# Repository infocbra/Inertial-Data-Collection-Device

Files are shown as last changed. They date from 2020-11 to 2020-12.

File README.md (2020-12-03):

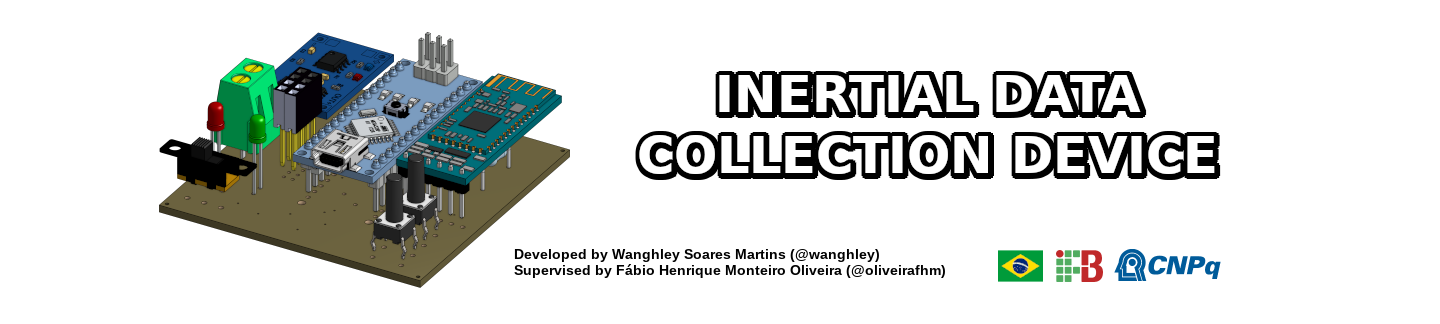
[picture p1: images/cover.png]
Inertial Data Collection Device






>  printed circuit board and code for collecting inertial data to research purposes of movements.

## About
Hardware developed to collect inertial data of humans (i.e. Accelerometer, Giroscope) and temperature in order to provide an open source hardware for researchs related to the analysis of human movements for many purposes.<br>
This project was tested in the diagnosis and prognosis of neuromotor diseases - Parkinson's disease mostly as part of the project of scientific research [**"Visualization Strategies to Online Big Data applied in individualized medicine"**](https://github.com/Wanghley/PIBIC-Strategies-Data-Visualization-Medicine).

## Requirements
| Dependency | Platform | Description |
| :--------- | -------- | :---------- |
| [arduino_2012](https://github.com/Wanghley/Inertial-Data-Collection-Device/blob/main/lib/arduino_2012.lbr) | eagle lib | arduino schematic and layout to **Eagle** project |
| [con-headers-jp](https://github.com/Wanghley/Inertial-Data-Collection-Device/blob/main/lib/con-headers-jp.lbr) | eagle lib | schematic and layout of female pin bars to **Eagle** project |
| [DIY modules](https://github.com/Wanghley/Inertial-Data-Collection-Device/blob/main/lib/diy-modules.lbr) | eagle lib | bluetooth adaptor fotoprint and symbol to **Eagle** project |
| [KRE](https://github.com/Wanghley/Inertial-Data-Collection-Device/blob/main/lib/kre.lbr) | eagle lib | borne connector fotoprint and symbol to **Eagle** project |
| [pinhead](https://github.com/Wanghley/Inertial-Data-Collection-Device/blob/main/lib/pinhead.lbr) | eagle lib | added in the **Eagle** project for auxiliary view of pin bars |
| [TimerOne 1.1.0](https://github.com/Wanghley/Inertial-Data-Collection-Device/blob/main/lib/TimerOne-1.1.0.zip) | arduino lib | allow running a periodic interrupt function based in finer PWM control |
| [MPU6050 0.2.1](https://github.com/Wanghley/Inertial-Data-Collection-Device/blob/main/lib/MPU6050-0.2.1.zip) | arduino lib | allow MPU6050 easy control and manipulation |
| [Wire](https://www.arduino.cc/en/reference/wire) | arduino lib | allow communication over I2C protocol |
| [SoftwareSerial](https://www.arduino.cc/en/Reference/softwareSerial) | arduino lib | allow serial communication on other digital pins of the Arduino |

## Bill of Materials
| # | Designator | Qty | Description | Obs |
| - | :--------- | --- | :---------- | :---------- | 
| 1 | R1, R2 | 2 | Resistor 220R 5% (1/4W) | Used for digital protection of bluetooth module RX |
| 2 | HC-05 | 1 | HC-05 Bluetooth Module | Module of Low supply consumption for prototype communication |
| 3 | PUSH | 2 | Push Button Long Head | Push button for hardware control and operation  |
| 4 | ON/OFF | 1 | 255sb sliding switch | Sliding switch to control energy supply of the prototype |
| 5 | LED1 | 1 | COM-09590 | 2.25 V Red LED 5mm Cylindrical indicates the hardware is ready for collection |
| 6 | LED2 | 1 | COM-09590 | 2.25 V green LED 5mm Cylindrical indicates the hardware operation mode and collection in process |
| 6 | Arduino Nano | Arduino Nano | | mother board and controller |
| 7 | KRE-2P | 1 | Borne Connector | Connector to the batery |
| 8 | BATTERY CHARGER | 1 | TP4056 | Power supply adn voltage regulator to the batery |

## Development
In order to run and contribute to the PCB development you must have **Eagle**  installed in your computer and then use the .sch to work on the circuit itself and the .brd to work in the layout design.

Now, for the development under de code of hardware control you must have Arduino IDE or similar to work on the .ino code.

## Authors
*   **Wanghley Soares Martins** - *junior researcher* - [wanghley](https://github.com/wanghley)
*   **Fábio Henrique Monteiro Oliveira** - *research advisor* - [oliveirafhm](https://github.com/oliveirafhm)

See also the list of [contributors](https://github.com/Wanghley/PIBIC-Strategies-Data-Visualization-Medicine/contributors) who participated in this project.

## License
This project is licensed under the MIT License - see the [LICENSE.md](LICENSE.md) file for details

## Acknowledge
*   Remember, the project is free for you to use, manipulate, change and distribute. However, I am just asking you to mention us in any copy, modification as the root of your development.
*   I would advice you to try out the hardware with an analysis of the result data.
*   If you want an easier software for hardware control, check out the [CONTROL SOFTWARE](https://github.com/Wanghley/PIBIC-Strategies-Data-Visualization-Medicine)

## Gallery
General view of the projected PCB. For more images go to [images/](https://github.com/Wanghley/Inertial-Data-Collection-Device/tree/main/images) and if you still want to see more you can see 3D views on [view/](https://github.com/Wanghley/Inertial-Data-Collection-Device/tree/main/view)
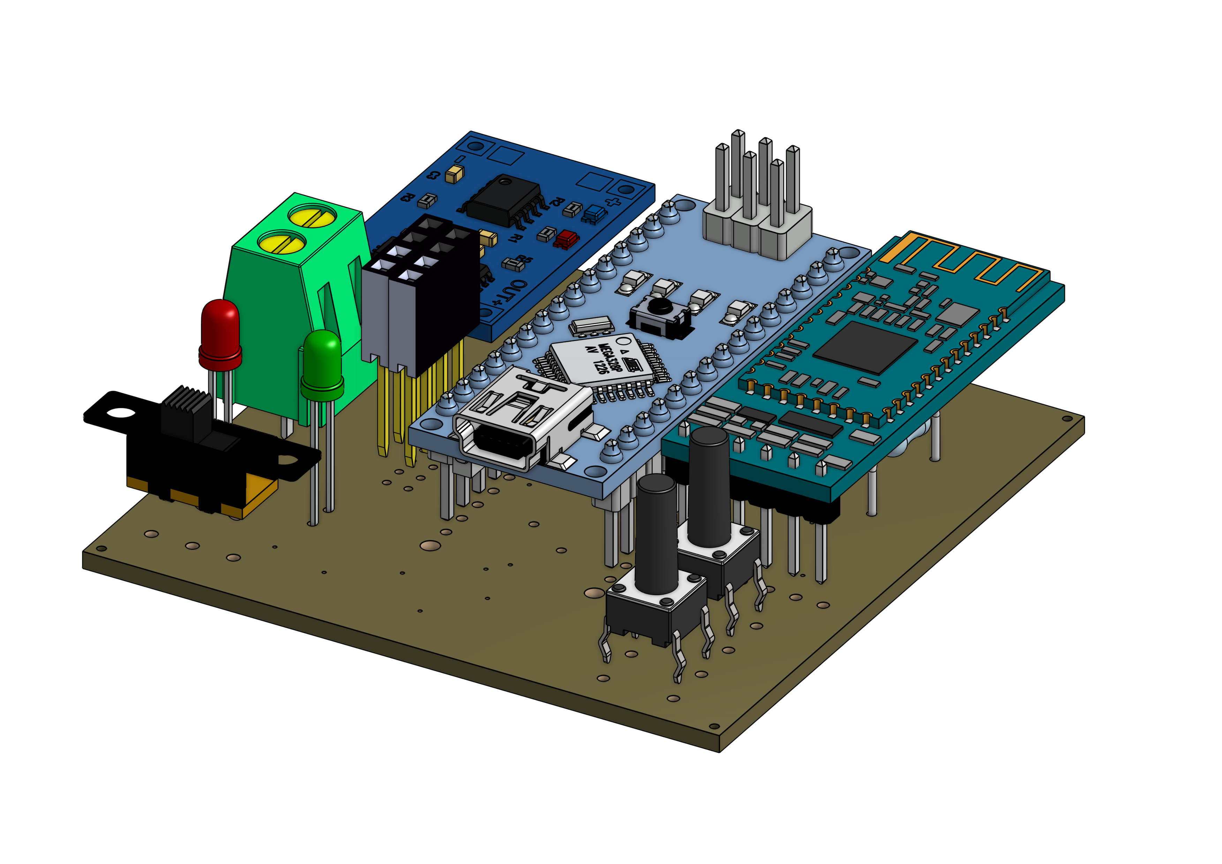
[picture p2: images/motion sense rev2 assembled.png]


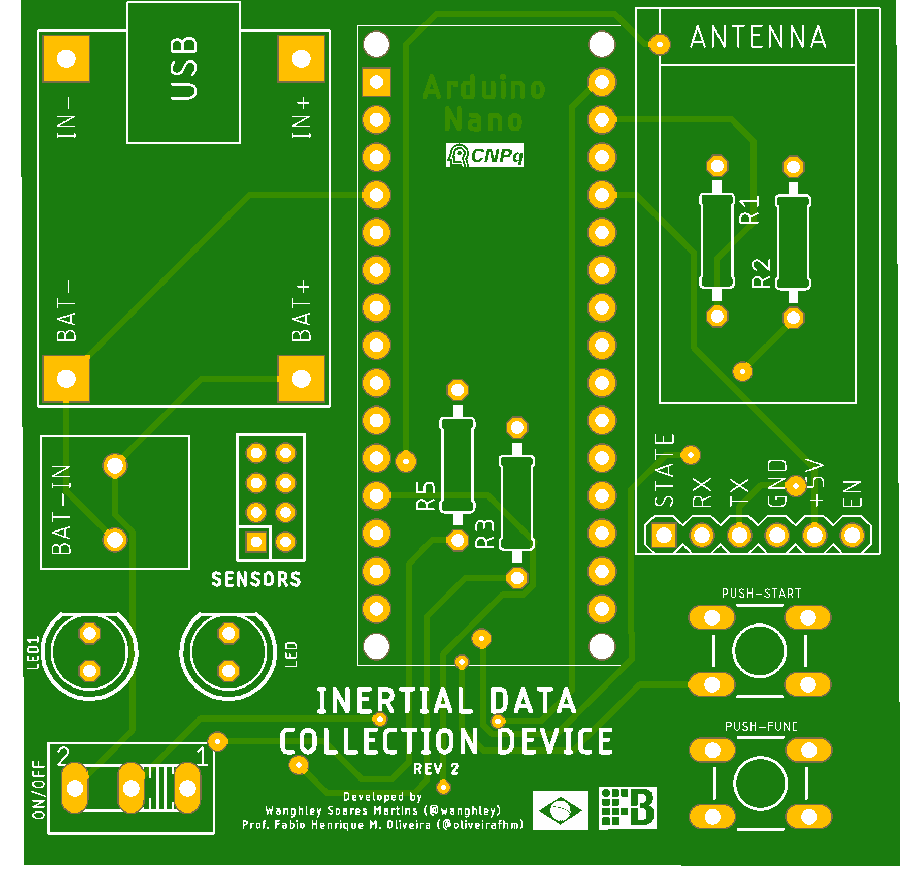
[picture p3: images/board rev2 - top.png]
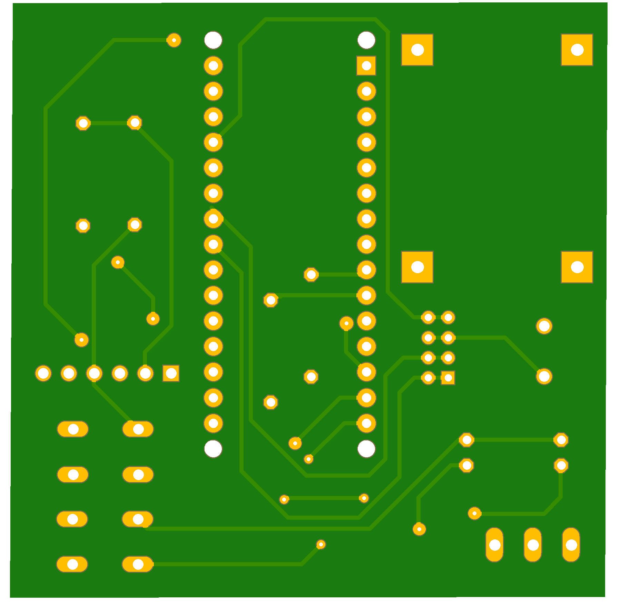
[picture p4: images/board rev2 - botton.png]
|  | | 
|-|-|

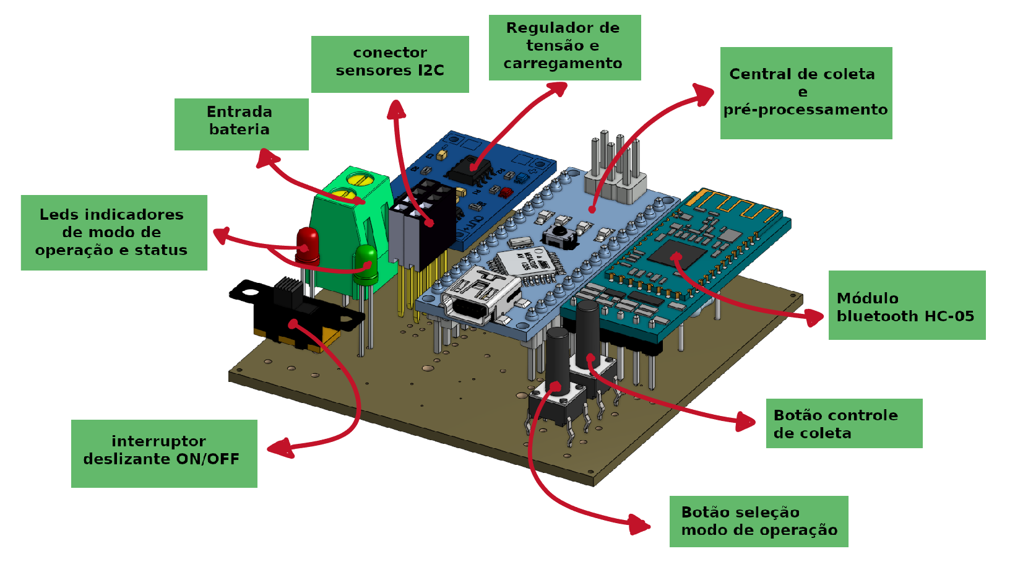
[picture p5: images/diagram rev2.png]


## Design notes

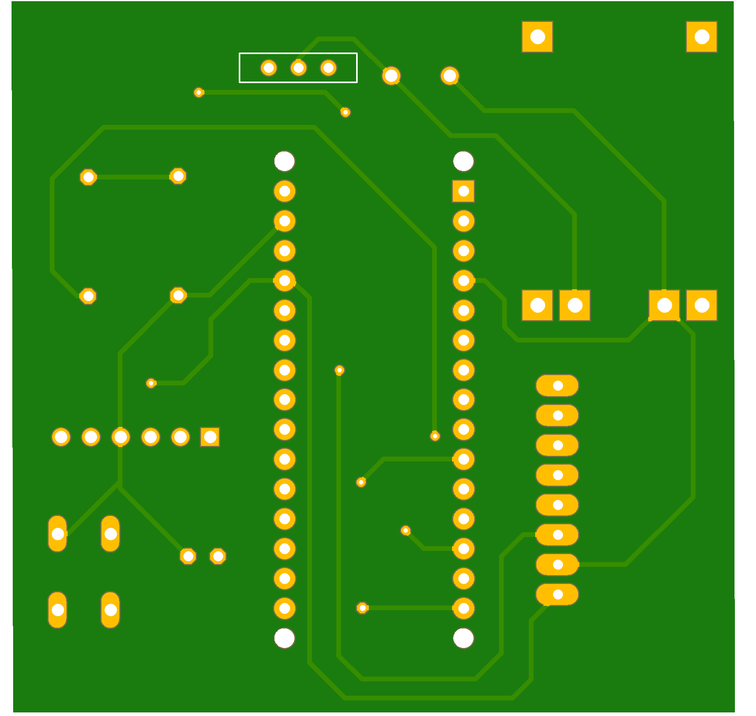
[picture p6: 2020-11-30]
images/board rev1 - botton.png

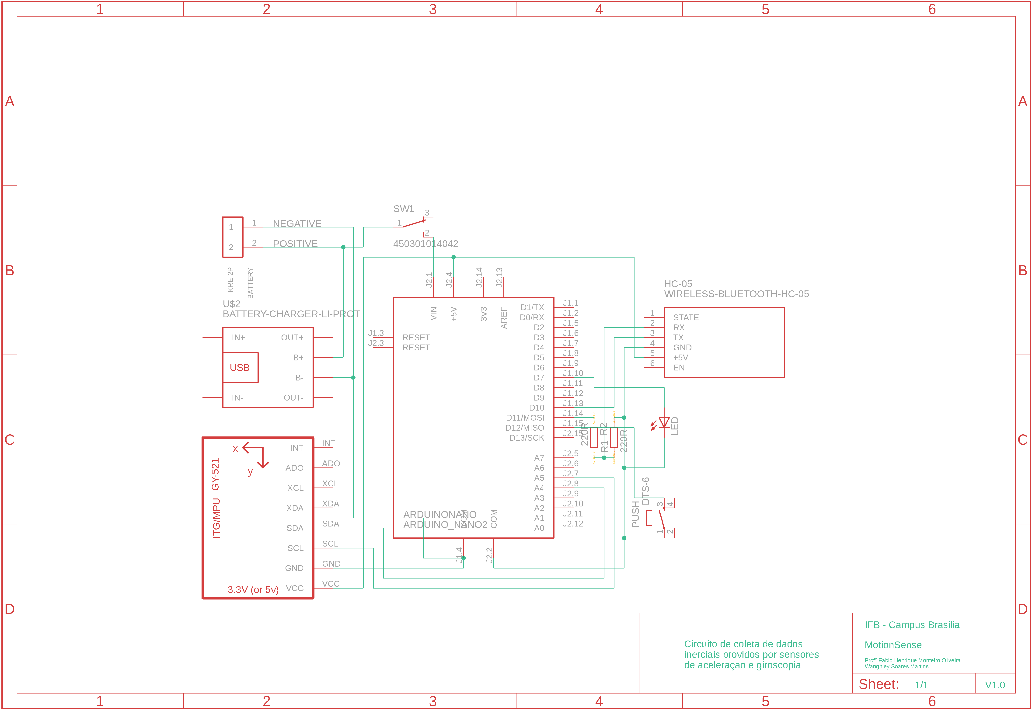
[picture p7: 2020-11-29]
images/sch rev1.png

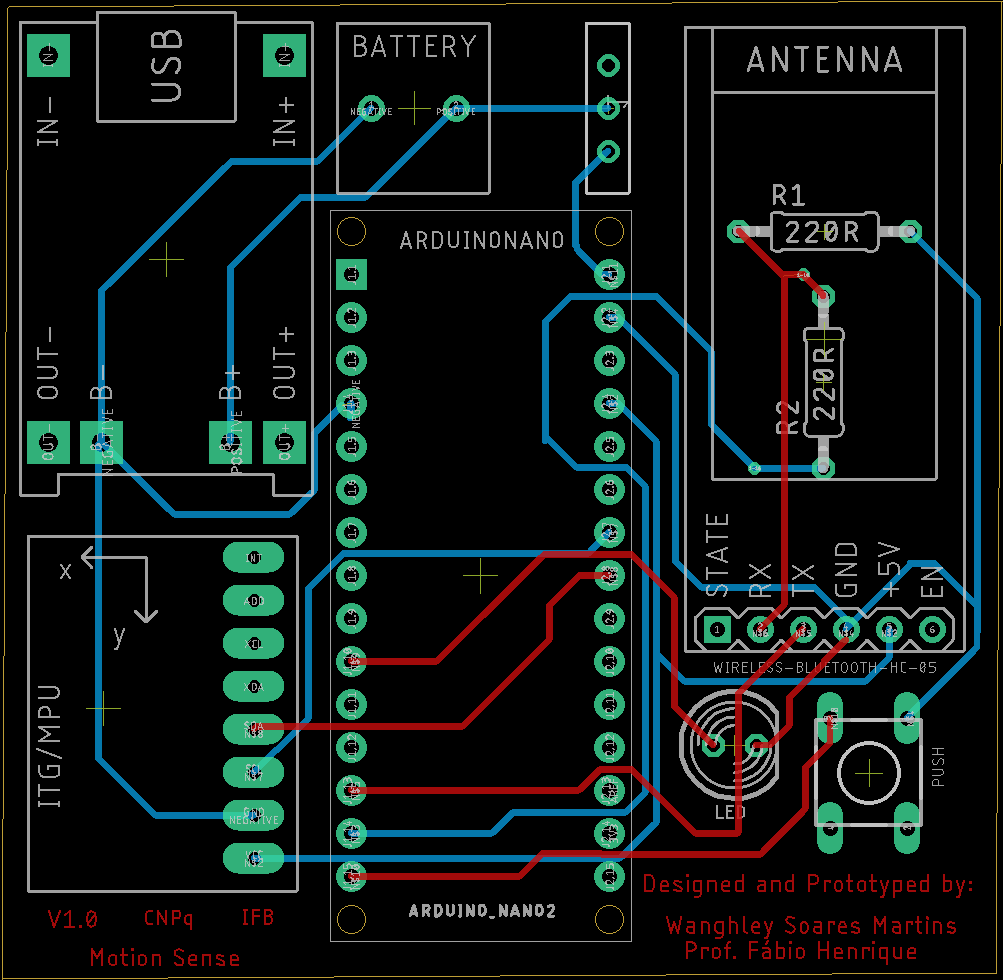
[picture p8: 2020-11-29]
images/pcb rev1.png

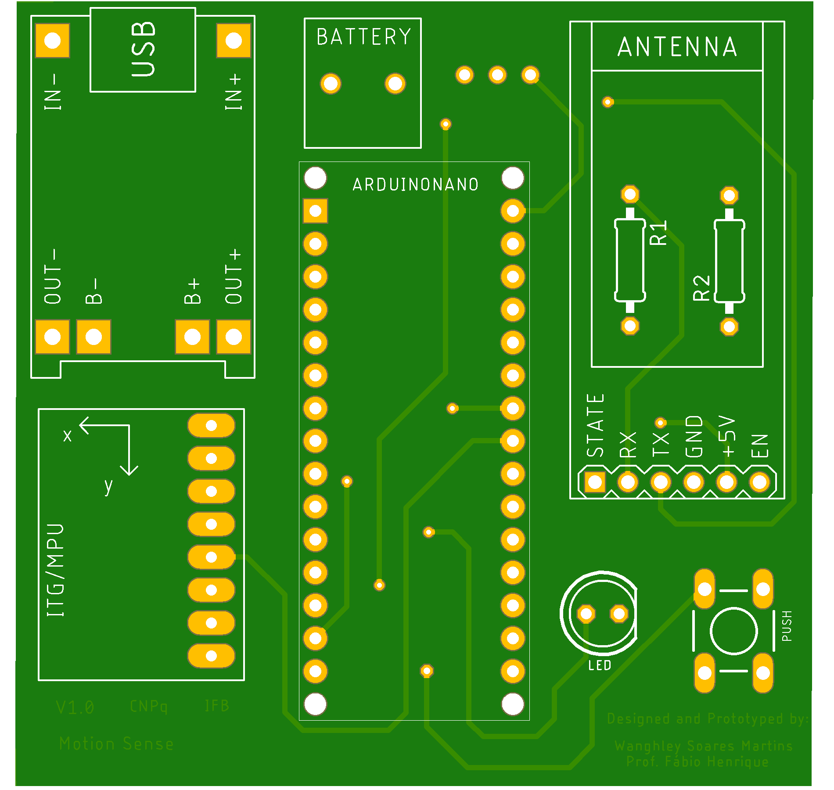
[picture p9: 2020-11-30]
images/board rev1 - top.png

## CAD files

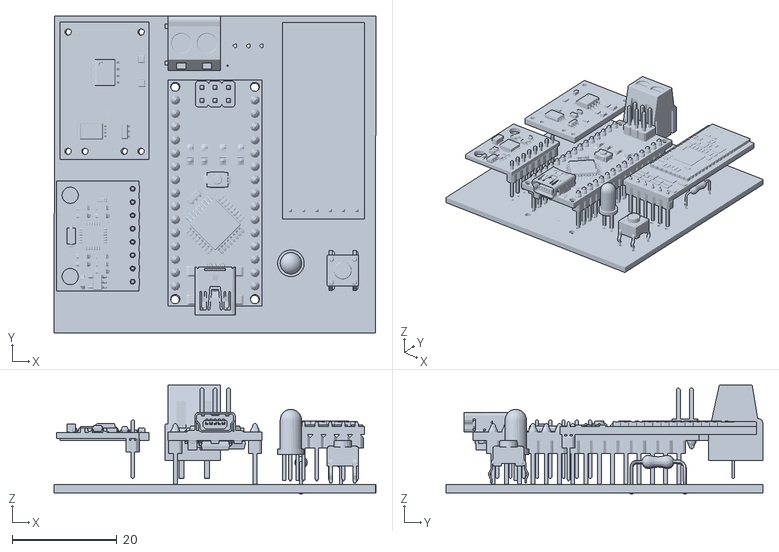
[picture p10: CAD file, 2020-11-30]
view/motion sense rev1 HQ.stl
61.6 x 60.6 x 20.8

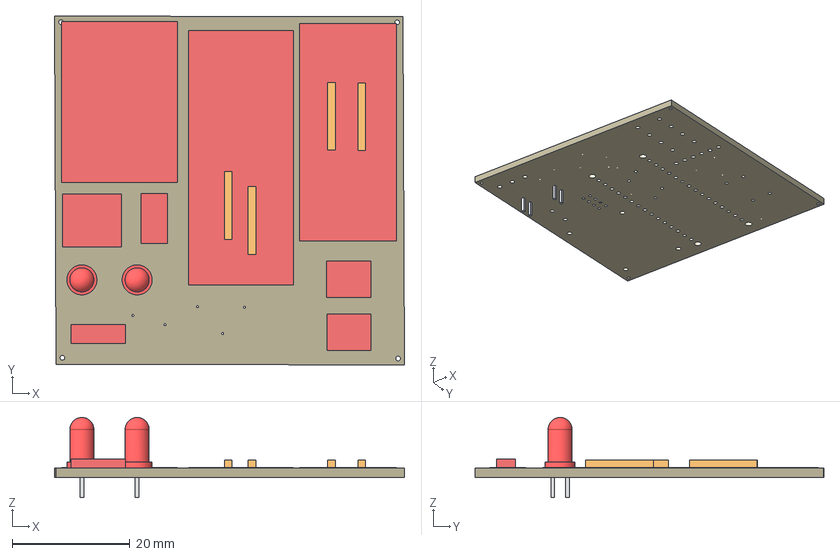
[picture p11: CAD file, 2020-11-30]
view/pcb-only.step
59.4 x 59.2 x 13.6 mm
Board
WIRELESS-BLUETOOTH-HC-05
collection indicator x 2
DTS-6 x 2
330R x 4
BATTERY-CHARGER-LI-5V
F-2X04-DIL-2MM_M
KRE-2P
255SB
ARDUINO_NANO2

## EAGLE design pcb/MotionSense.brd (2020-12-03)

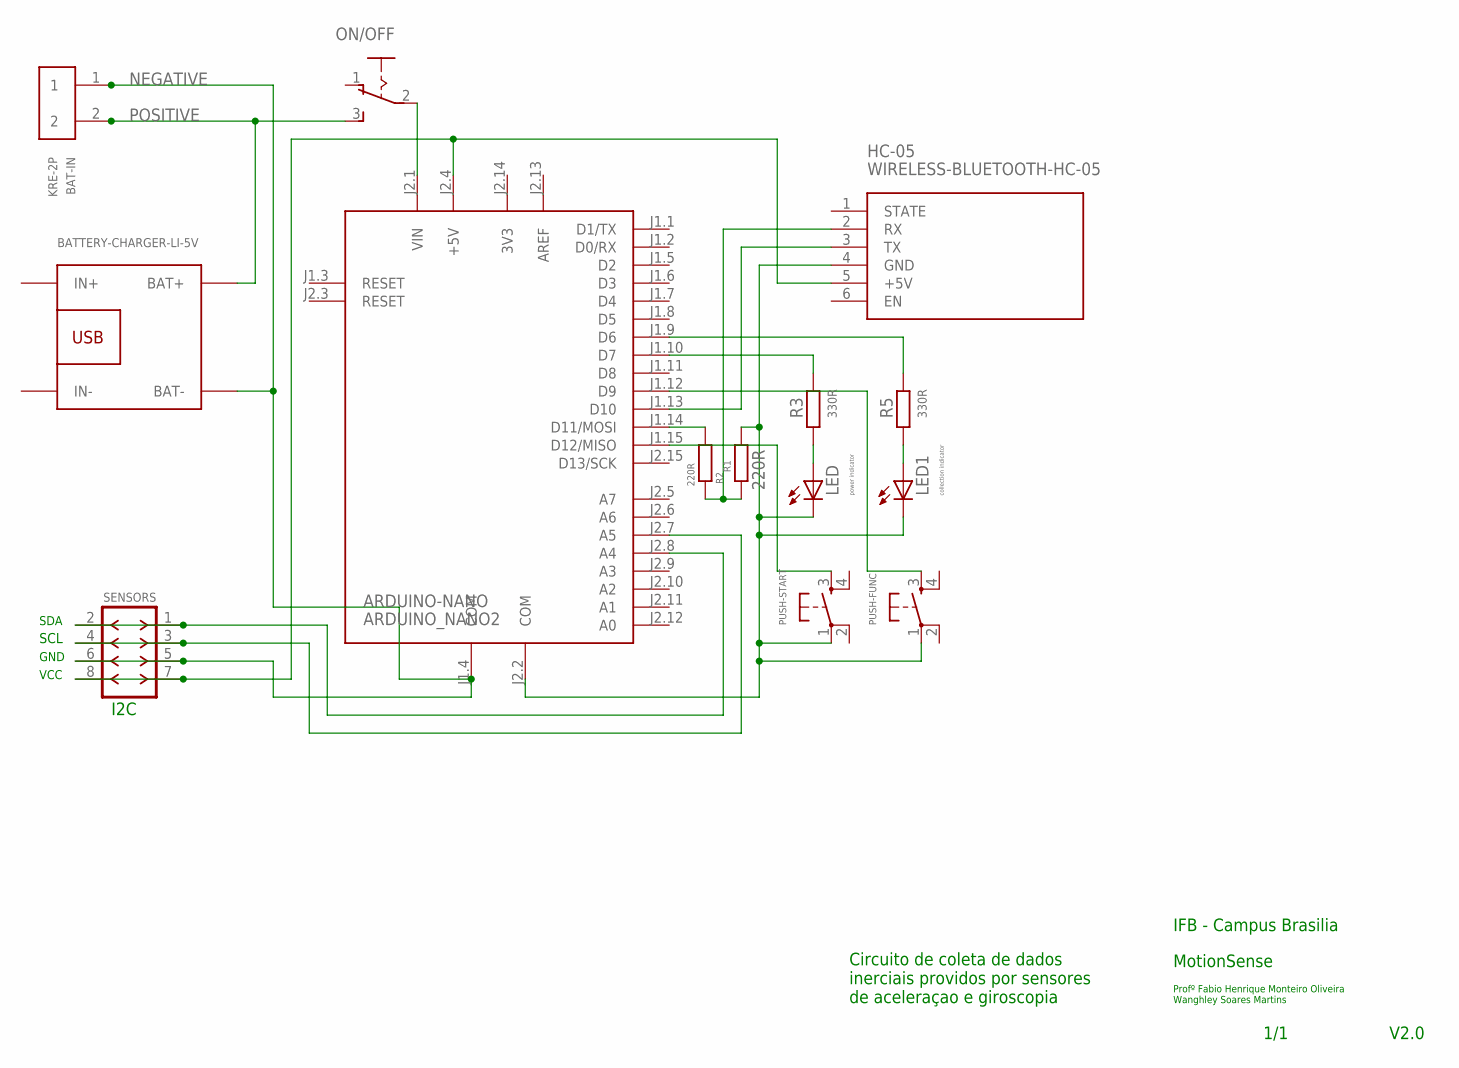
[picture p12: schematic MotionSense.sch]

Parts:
ARDUINO-NANO: ARDUINO_NANO2
BAT-IN: KRE-2P
HC-05: WIRELESS-BLUETOOTH-HC-05
LED: power indicator; LED5MM
LED1: collection indicator; LED5MM
ON/OFF: 255SB
PUSH-FUNC: DTS-6
PUSH-START: DTS-6
R1, R2: 220R; 0207/10
R3, R5: 330R; 0207/10
SENSORS: F-2X04-DIL-2MM_M; DIL-2MM-2X04_M
U$1: BATTERY-CHARGER-LI-5V

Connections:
3V3: ARDUINO-NANO.J2.14 (3V3)
AREF: ARDUINO-NANO.J2.13 (AREF)
unnamed: LED.A, R3.1
unnamed: ARDUINO-NANO.J2.4 (+5V), HC-05.5 (+5V), SENSORS.7, SENSORS.8
unnamed: ARDUINO-NANO.J1.14 (D11/MOSI), R2.1
unnamed: ARDUINO-NANO.J2.2 (COM), HC-05.4 (GND), LED.K (C), LED1.K (C), PUSH-FUNC.1, PUSH-START.1, R1.2
unnamed: ARDUINO-NANO.J1.13 (D10), HC-05.3 (TX)
unnamed: HC-05.2 (RX), R1.1, R2.2
unnamed: ARDUINO-NANO.J2.7 (A5), SENSORS.3, SENSORS.4
unnamed: ARDUINO-NANO.J2.8 (A4), SENSORS.1, SENSORS.2
unnamed: ARDUINO-NANO.J1.10 (D7), R3.2
unnamed: ARDUINO-NANO.J1.15 (D12/MISO), PUSH-START.3
unnamed: ARDUINO-NANO.J2.1 (VIN), ON/OFF.2
unnamed: ARDUINO-NANO.J1.12 (D9), PUSH-FUNC.3
unnamed: ARDUINO-NANO.J1.9 (D6), R5.2
unnamed: LED1.A, R5.1
NEGATIVE: ARDUINO-NANO.J1.4 (COM), BAT-IN.1, SENSORS.5, SENSORS.6, U$1.BAT-
POSITIVE: BAT-IN.2, ON/OFF.3 (S), U$1.BAT+

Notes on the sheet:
Circuito de coleta de dados inerciais providos por sensores de aceleraçao e giroscopia
MotionSense
IFB - Campus Brasilia
Profº Fabio Henrique Monteiro Oliveira Wanghley Soares Martins
V2.0
1/1
I2C
VCC
GND
SCL
SDA

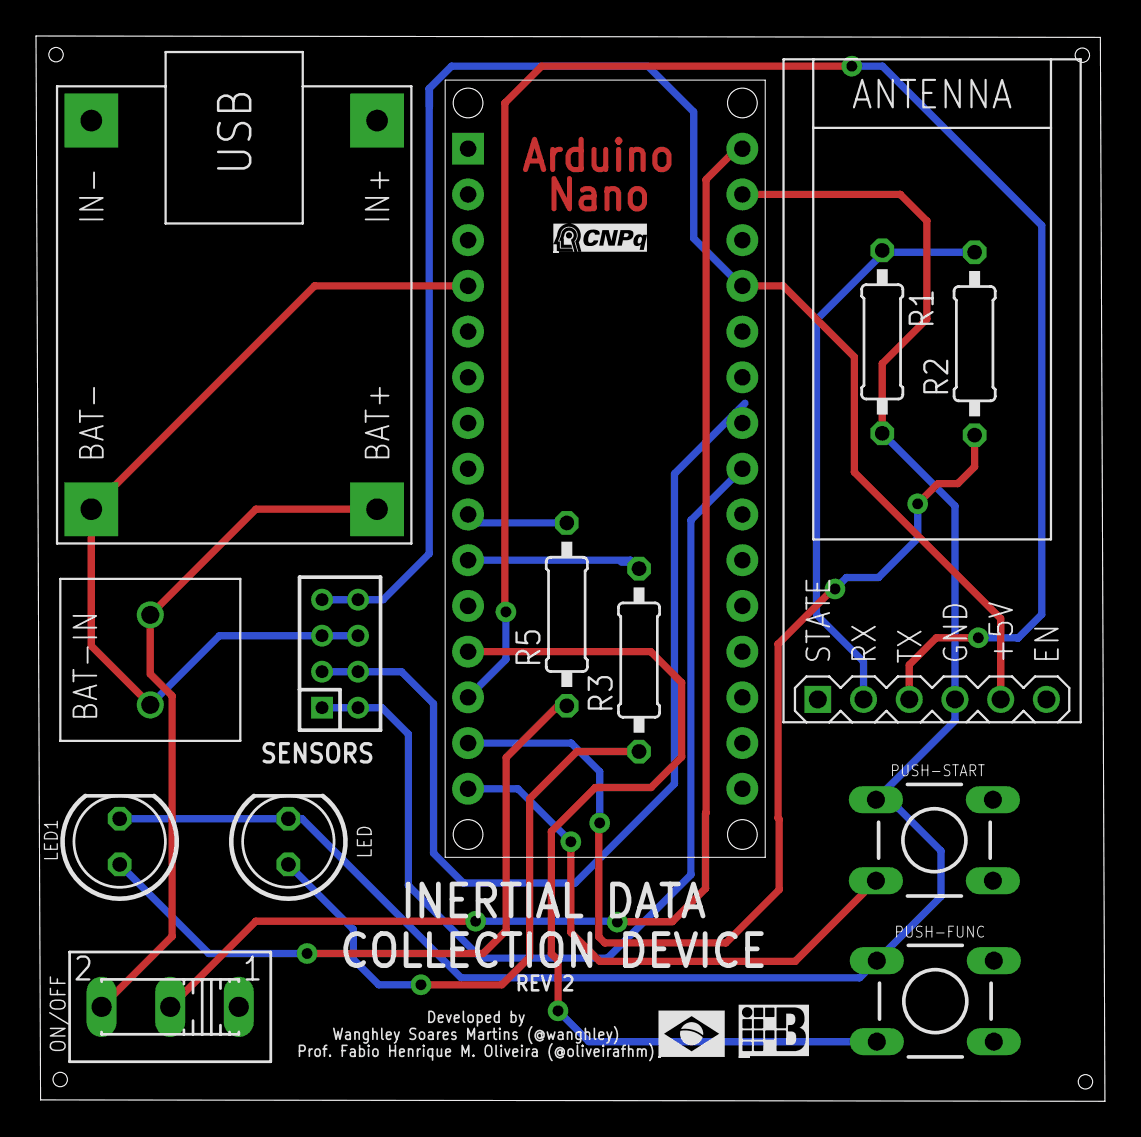
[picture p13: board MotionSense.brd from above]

Board: 2 copper layers, 59.4 x 59.2 mm, 14 parts (0 on the bottom side), 16 nets.

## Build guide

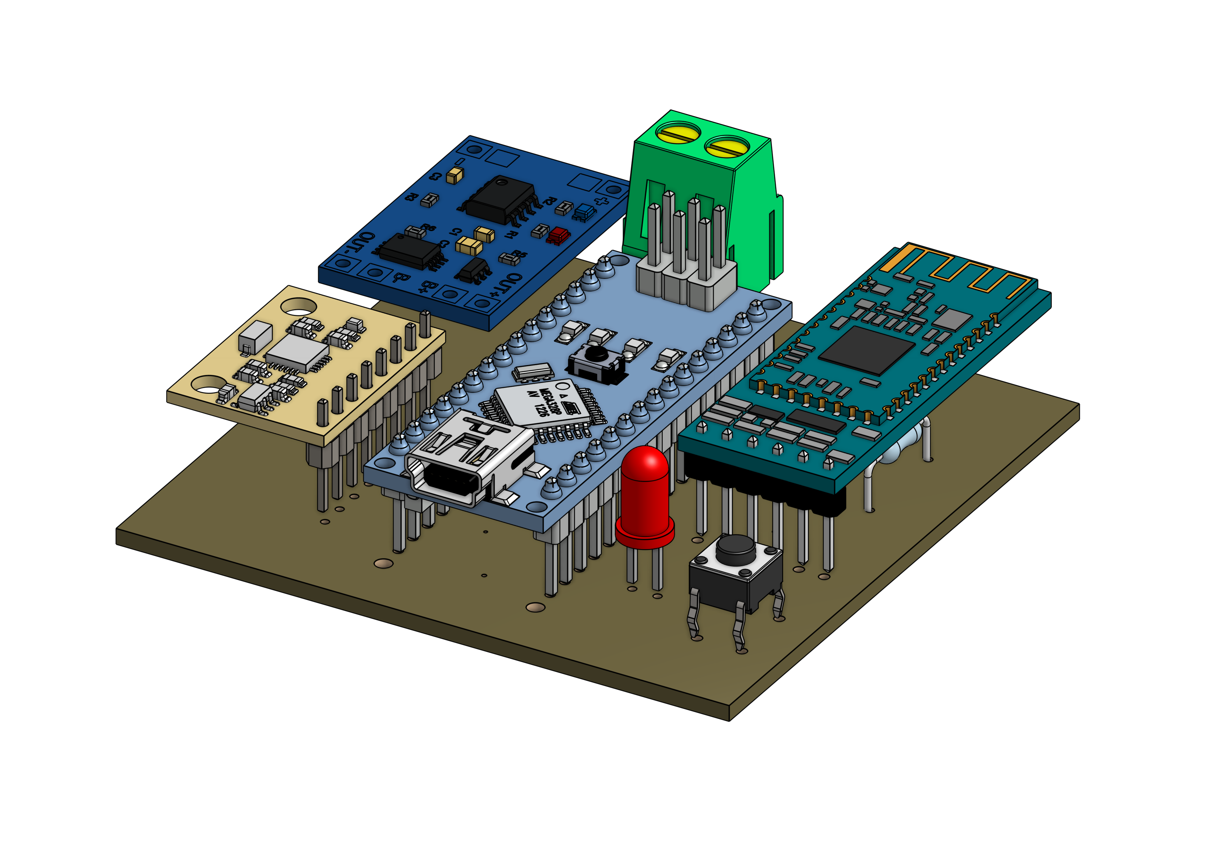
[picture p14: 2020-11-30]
images/motion sense rev1 assembled.png

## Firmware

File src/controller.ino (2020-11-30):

/*
AUTHOR: Wanghley Soares Martins (@wanghley)
DATE: April 11, 2019
CONTACT: wanghleys@gmail.com
REV1: Fabio Henrique, Lissa Ximenes
DATE: Sep 19, 2019
REV2: Wanghley Martins
DATE: Nov 19, 2020
*/
#include <TimerOne.h>       // Library for timer interrupt
#include <MPU6050.h>        // Standard library for manipulation on the MPU6050
#include <Wire.h>           // Control library of the I²C protocol, used by the MPU6050
#include <SoftwareSerial.h> // Bluetooth control library

#define BTN 12
#define LED 7

SoftwareSerial BTSerial(10, 11); // RX | TX

const int MPU = 0x68; // MPU6050 address on the I²C bus (available in datasheet)
volatile bool visualization = false; // Variable is loaded into the "RAM memory" of the microcontroller
boolean controle = true, initiate = false; // Variable of flow control
int ledstate = 0; // LED state indicator
double AcX, AcY, AcZ, Tmp, GyX, GyY, GyZ; // Variables used to store data
char a, c='-1', c1='-1';
unsigned long current;
unsigned long last;
volatile bool flag = false;
bool flagCopy;
volatile unsigned long interval = 0;
unsigned long intervalCopy;
long Micros;

void setup()
{
    /*Bluetooth comunication: 
      Module - HC-05
      Password - 1234
    */
    Wire.begin();                // I²C communication starts
    Wire.beginTransmission(MPU); // Indicates the address of the MPU to start communication
    Wire.write(0x6B);            // Indicates the MPU that the communication will start
    Wire.write(0);               // Indicates the MPU that wants to leave the communication on standby
    Wire.endTransmission(true);  // Disables communication

    Serial.begin(57600);
    Serial.println("Open Parkinson's Diagnostic Device");
    BTSerial.begin(57600); // HC-05 default speed in AT command more

    // starts the sample rate by time (clock)
    Timer1.initialize(20000); // Adjusted for 50hz = 10⁶ / 50 = 20,000µs
    Timer1.attachInterrupt(changeFlag); // Indicates the function that will be called every 20,000ms
    
    pinMode(BTN,INPUT_PULLUP);
    pinMode(LED,OUTPUT);
    digitalWrite(LED,LOW);
}

//Função que imprime os dados lidos pelo MPU6050 a cada chamada da interrupção
void changeFlag(){
  if (visualization){
    flag = true; // active data display
    Micros = micros();
  }    
}

void loop(){
  if(digitalRead(BTN)==LOW){
   if(initiate==true){
     Serial.println("Finalizando...");
     initiate = false;
     BTSerial.write("stop#");
     digitalWrite(LED,LOW);
   }else{
     Serial.println("initiatendo...");
     initiate=true;
     digitalWrite(LED,HIGH);
   }
   delay(350);
  }
    
  if (initiate){ 
    if(Serial.available()){
     a = Serial.read();
     if(a=='f'){
       BTSerial.write("stop#");
       BTSerial.flush();//Descarrega o buffer
       Serial.println("Comunication Closed!");
       visualization = false;
     }
    }

    noInterrupts();// 
    flagCopy = flag;
    flag = false;
    intervalCopy = interval;
    interval = 0;
    interrupts();
    if (flagCopy){
      printData();
    }
    int val = BTSerial.read();
    
    c='-1';
    c1='-1';
    if (val != -1){
        c = val;
    }
    
    if (c == 's'){
      Serial.println("Comunication started!\nWaiting final handshake");
      BTSerial.write("ok#");
      BTSerial.flush(); //Limpar buffer
      while (controle){
        val = BTSerial.read();
        if (val != -1){
          c1 = val;
          if(c1=='c'){
            controle = false;
            Serial.println("Data collection started!");
            visualization = true;
          }
        }
      }
    }
    
    if (visualization){
        Wire.beginTransmission(MPU); //Indica a retomada na comunicação i²c
        Wire.write(0x3B);            /*initiate o registrador do MPU6050, indicando que irá receber dados*/
        Wire.endTransmission(false); //initiate a comunicação estável novamente
        //Solicita dados do sensor
        Wire.requestFrom(MPU, 14, true);
        getData();
        // Keep reading from HC-05 and send to Arduino Serial Monitor
    }

    if (Serial.available()){
      a = Serial.read();
      if (a == 'f'){
        BTSerial.write("stop#");
        BTSerial.flush(); //Descarrega o buffer
        Serial.println("Canal fechado..");
        visualization = false;
      }
    }
  }
}

//Função que recebe os dados do MPU6050 e
//faz as conversões do valor bruto para acc = g e gy = º/seg
void getData(){
  //Armazena o valor dos sensores nas variaveis correspondentes
  AcX = Wire.read() << 8 | Wire.read(); //0x3B (ACCEL_XOUT_H) & 0x3C (ACCEL_XOUT_L)
  AcY = Wire.read() << 8 | Wire.read(); //0x3D (ACCEL_YOUT_H) & 0x3E (ACCEL_YOUT_L)
  AcZ = Wire.read() << 8 | Wire.read(); //0x3F (ACCEL_ZOUT_H) & 0x40 (ACCEL_ZOUT_L)
  Tmp = Wire.read() << 8 | Wire.read(); //0x41 (TEMP_OUT_H) & 0x42 (TEMP_OUT_L)
  GyX = Wire.read() << 8 | Wire.read(); //0x43 (GYRO_XOUT_H) & 0x44 (GYRO_XOUT_L)
  GyY = Wire.read() << 8 | Wire.read(); //0x45 (GYRO_YOUT_H) & 0x46 (GYRO_YOUT_L)
  GyZ = Wire.read() << 8 | Wire.read(); //0x47 (GYRO_ZOUT_H) & 0x48 (GYRO_ZOUT_L)
  
  
  //Dados recebidos em 2g
  AcX = AcX / 16384.0;        //Conversão para G
  AcY = AcY / 16384.0;        //Conversão para G
  AcZ = AcZ / 16384.0;        //Conversão para G
  Tmp = Tmp / 340.00 + 36.53; //Conversão para ºC
  GyX = GyX / 250.0;          //Conversão para º/seg
  GyY = GyY / 250.0;          //Conversão para º/seg
  GyZ = GyZ / 250.0;          //Conversão para º/seg
}

void printData(){
  BTSerial.print((String)Micros+","+(String)AcX+","+(String)AcY+","+(String)AcZ+","+(String)GyX+","+(String)GyY+","+(String)GyZ+","+(String)Tmp+"#");
  BTSerial.flush();
//  Serial.println((String)Micros+","+(String)AcX+","+(String)AcY+","+(String)AcZ+","+(String)GyX+","+(String)GyY+","+(String)GyZ+","+(String)Tmp+"#");
}

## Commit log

2020-11-29 [ADD] images prototype version 1.0
2020-11-29 [ADD] version 1 prototype finished
    [MotionSense.brd, MotionSense.sch]
2020-11-29 [UPDATE] bug correction and library problems
    2 leds
    2 push btns
    refactor sensors I2C connector
    [MotionSense.sch]
2020-11-29 [UPDATE]libraries addition to next version of PCB
2020-11-30 [UPDATE]connection bug fix
    [MotionSense.sch]
2020-11-30 [UPDATE] PCB update v2
    [MotionSense.brd]
2020-11-30 [UPDATE]adding dimension measurement
    The measurement is in mm
    [MotionSense.brd]
2020-11-30 [UPDATE] drilling addition
    [MotionSense.brd]
2020-11-30 [ADD]board manufacturing picture REV2 addition
2020-11-30 [UPDATE] connection missing bug fixing
    connection to the ground was not done.
    [MotionSense.brd]
2020-11-30 [ADD]cam outputs for gerber files generation
    [copper_bottom.gbr, copper_top.gbr, drill_1_16.xln, gerber_job.gbrjob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]
2020-11-30 [ADD]pcb 3D visualization file
    [pcb-only.step]
2020-11-30 [ADD]PCB with assembled parts to preview
    3D visualization of the real prototype of Inertial Data Collection Device
2020-11-30 [ADD]glb pcb+assemblies view
2020-11-30 [ADD] bitmap board assembled
2020-11-30 [UPDATE]bill materials addition
2020-11-30 [ADD]prototype rev1 SQ 3D view
2020-11-30 [ADD]prototype rev1 HQ 3D view
    [motion sense rev1 HQ.stl]
2020-12-03 [UPDATE]pads correction to up to 1.4mm
    [MotionSense.brd]
2020-12-03 [UPDATE]gbr file update
    [copper_bottom.gbr, gerber_job.gbrjob]

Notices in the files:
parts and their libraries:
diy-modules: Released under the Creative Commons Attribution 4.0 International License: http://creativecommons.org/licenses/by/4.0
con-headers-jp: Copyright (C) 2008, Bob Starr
